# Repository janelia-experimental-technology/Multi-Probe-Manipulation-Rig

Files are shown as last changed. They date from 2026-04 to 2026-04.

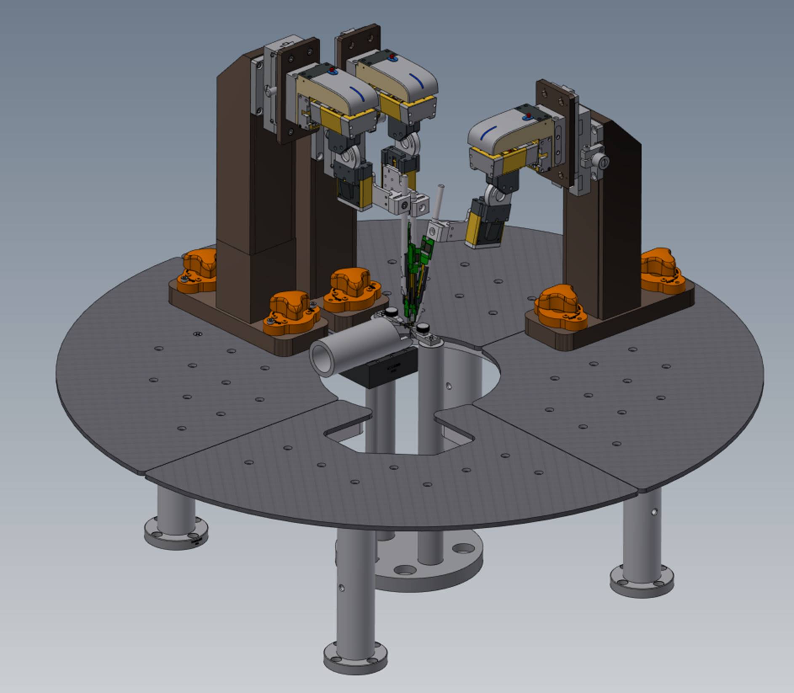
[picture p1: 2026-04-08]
Manipulator Rig.jpg

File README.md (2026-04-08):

### Multi-probe Manipulation Rig

Neural probe manipulation requires precise manipulation to avoid errors and optimize good placement for signal development. Janelia researchers and the Janelia Experimental Technology group have developed a multi-probe manipulation rig for such experiments with rodents. The base surface is magnetic stainless steel and the manipulator towers can be freely moved then locked in place with magnetic clamps for rough positioning. Sensapex 3 axis micromanipulators then provide precise positioning. Adapter designs for the manipulator include holders for Neuropixels probes.   

Opportunity: Free to make for Non-Profit Research by downloading the design here. See included hardware license.

Rights and designs available for Commercial License. Janelia makes no endorsements or guarantees of licensee products.

For inquiries, please contact innovation@janelia.hhmi.org and reference this repository.

To cite the designs, please use DOI: https://doi.org/10.25378/janelia.31964007

Supersedes Flintbox ID: 2020-004

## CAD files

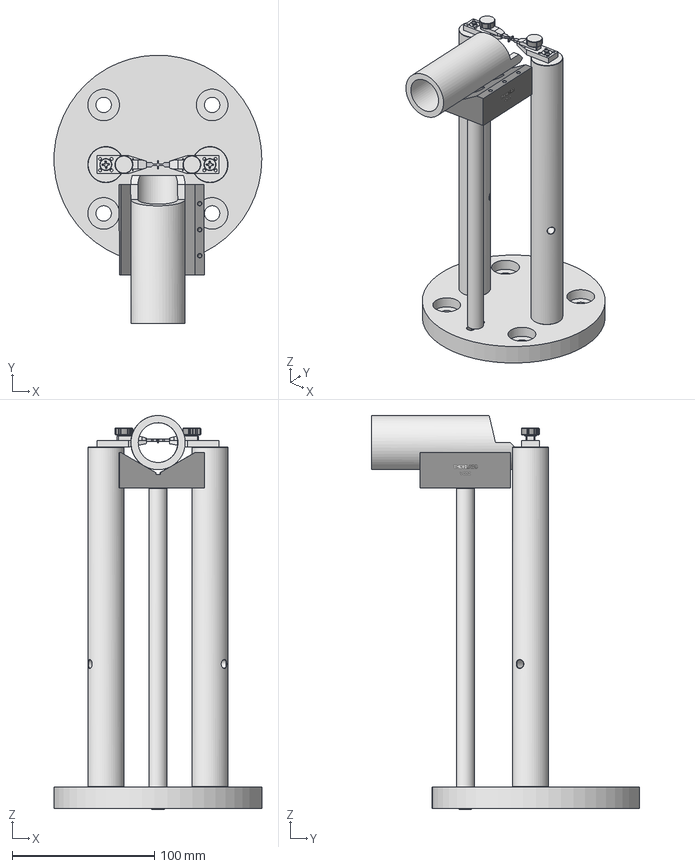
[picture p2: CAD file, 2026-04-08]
ASSEMBLY DRAWINGS AND MODEL/J008192 PTR V2 HEAD POST AND MOUNTING BARS Rev -.stp
145.9 x 188.6 x 276.8 mm
J005774 x 2
J005776 x 2
91771A197 x 2
92141A009 x 2
91185A440 x 2
91841A009 x 2
J007751 x 2
VC3C
PTR Mouse Tube
J008194
J007279
J006229
92240A539 x 2
92196A539

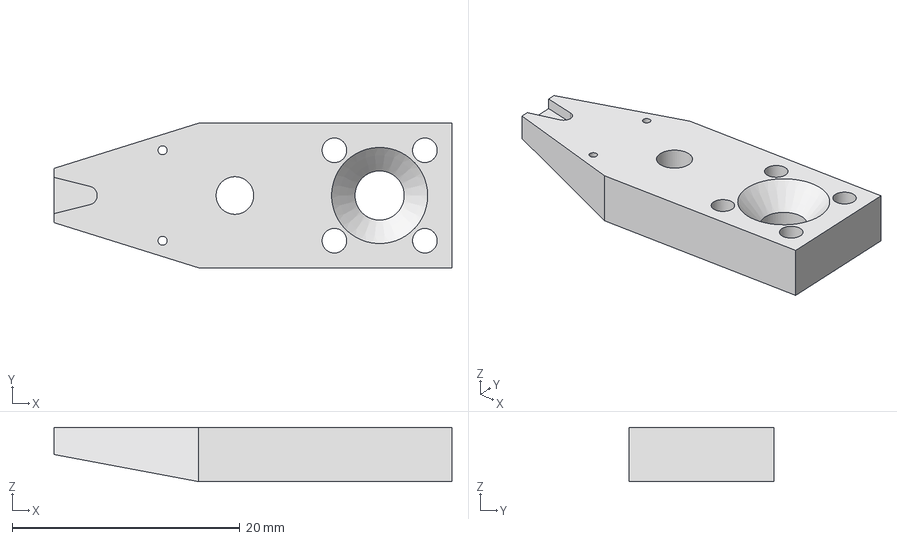
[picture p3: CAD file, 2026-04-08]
PART DRAWINGS AND MODELS/J005774 HeadPostHolderBottom Rev -.stp
34.9 x 12.7 x 4.76 mm

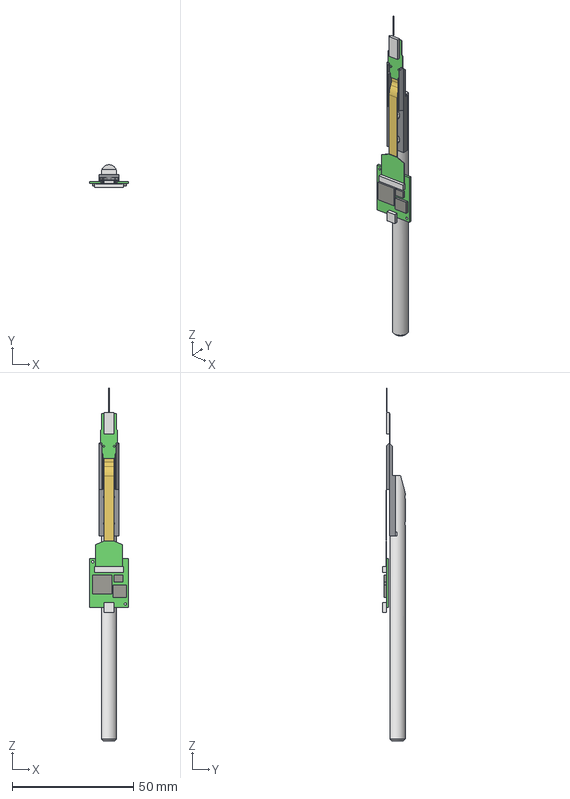
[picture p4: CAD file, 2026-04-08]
ASSEMBLY DRAWINGS AND MODEL/J007802 NEUROPIXELS 3A ENGINEERING PROTOTYPE PROBE AND ROD HOLDER Rev -.stp
16.0 x 9.32 x 145.3 mm
NEUROPIXEL HEADSTAGE PCB
J007803
J007626
92010A003 x 2

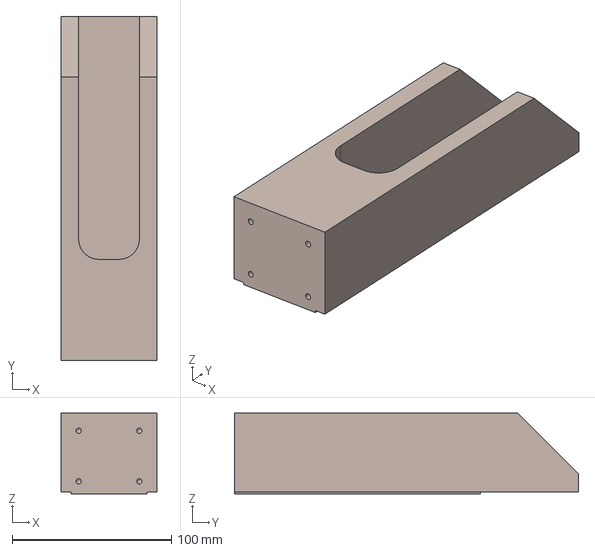
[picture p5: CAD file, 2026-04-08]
PART DRAWINGS AND MODELS/J007471 PTR V2 Z MOUNT Rev -.stp
60.3 x 215.9 x 50.8 mm

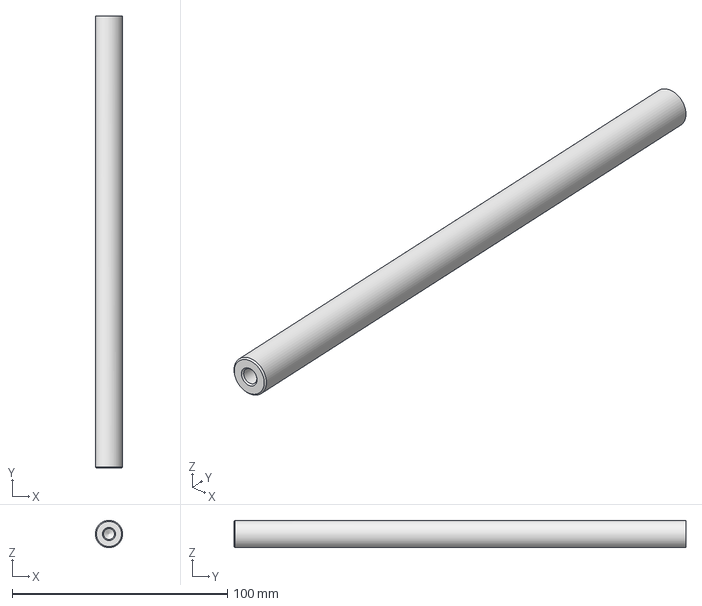
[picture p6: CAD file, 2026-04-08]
PART DRAWINGS AND MODELS/J008194 TR10-AI Rev -.stp
12.7 x 210.0 x 12.7 mm

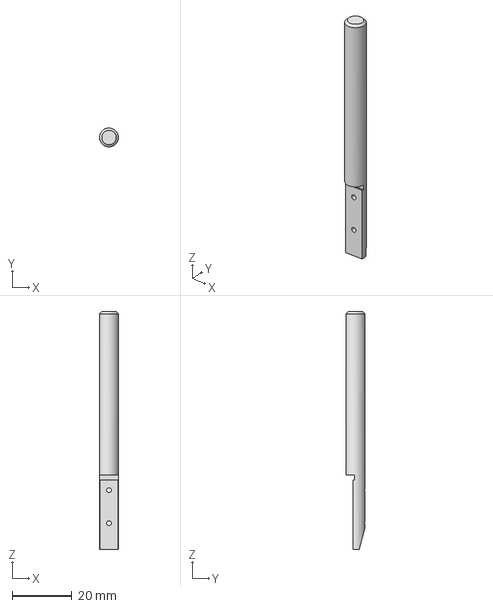
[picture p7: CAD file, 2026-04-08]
PART DRAWINGS AND MODELS/J007474 PTR PROBE MOUNT ROD Rev -.stp
6.35 x 6.35 x 79.4 mm

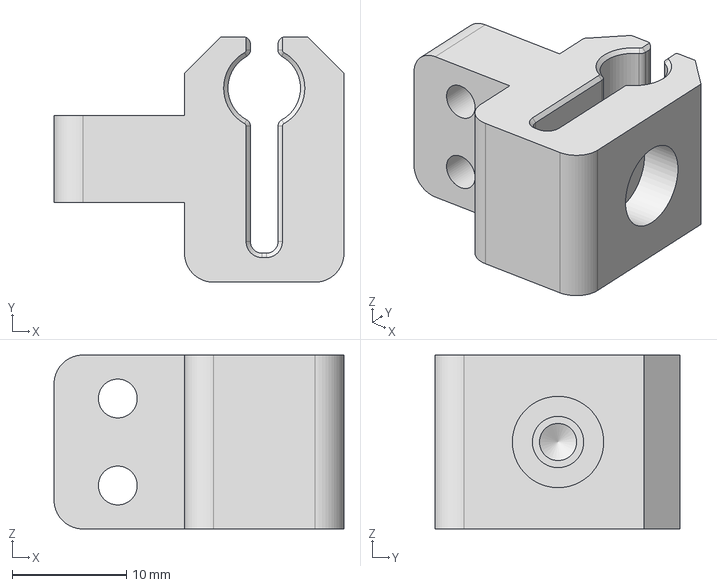
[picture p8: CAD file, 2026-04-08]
PART DRAWINGS AND MODELS/J007475 PTR V2 ROD MOUNT 0_250 DIA Rev -.stp
25.4 x 21.5 x 15.2 mm

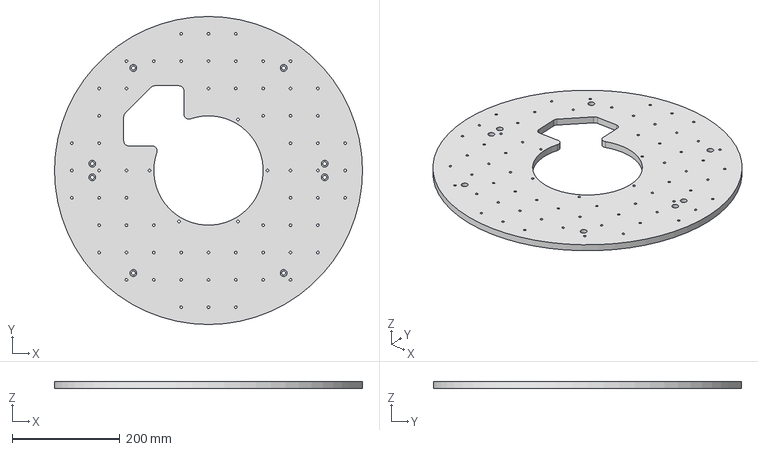
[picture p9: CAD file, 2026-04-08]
PART DRAWINGS AND MODELS/J006218 PTR RAISED PLATFORM Rev A.stp
572.3 x 572.3 x 12.7 mm

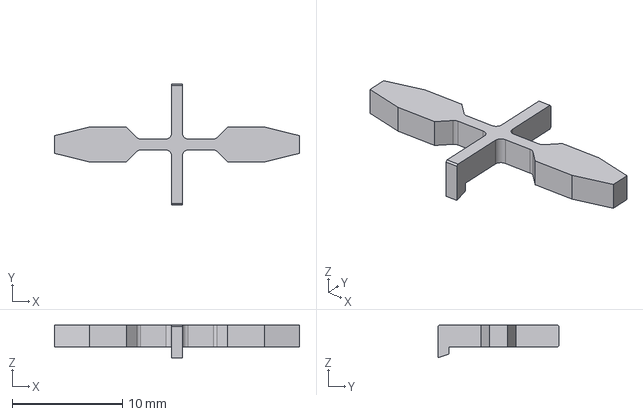
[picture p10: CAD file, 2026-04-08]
PART DRAWINGS AND MODELS/J007279 NARROWED CENTER X HEADBAR Rev -.stp
22.2 x 11.0 x 2.96 mm

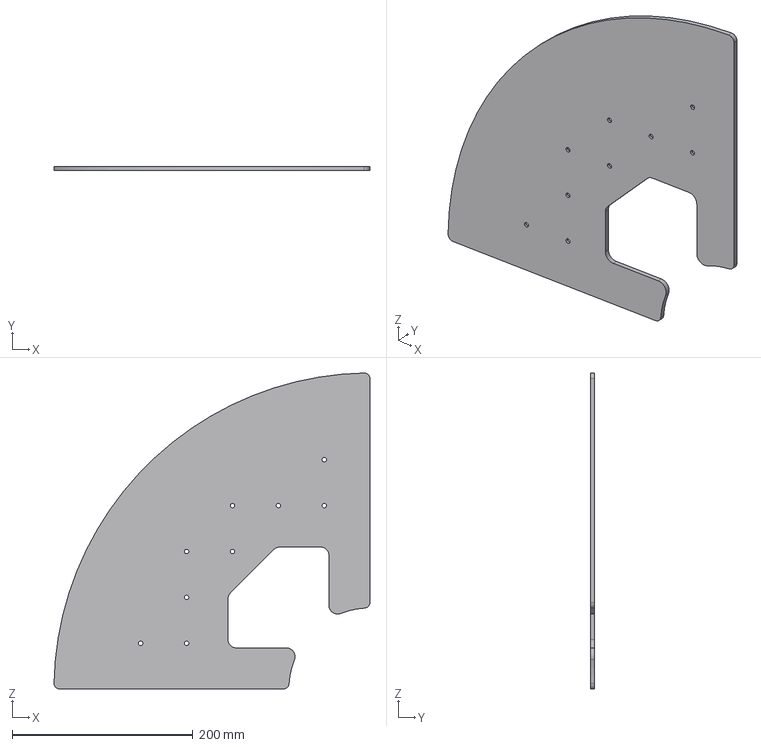
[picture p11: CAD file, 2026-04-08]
PART DRAWINGS AND MODELS/J007541 PTR MBASE CUTOUT Rev -.stp
349.7 x 4.76 x 349.7 mm

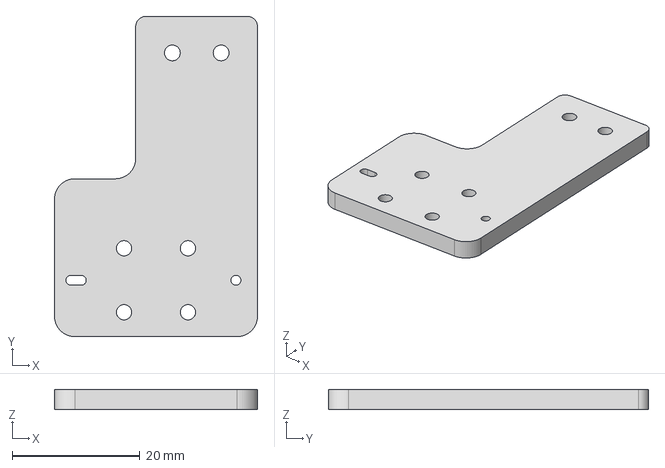
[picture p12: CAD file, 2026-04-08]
PART DRAWINGS AND MODELS/J007476 PTR MANIPULATOR OFFSET PLATE Rev -.stp
31.8 x 50.1 x 3.17 mm

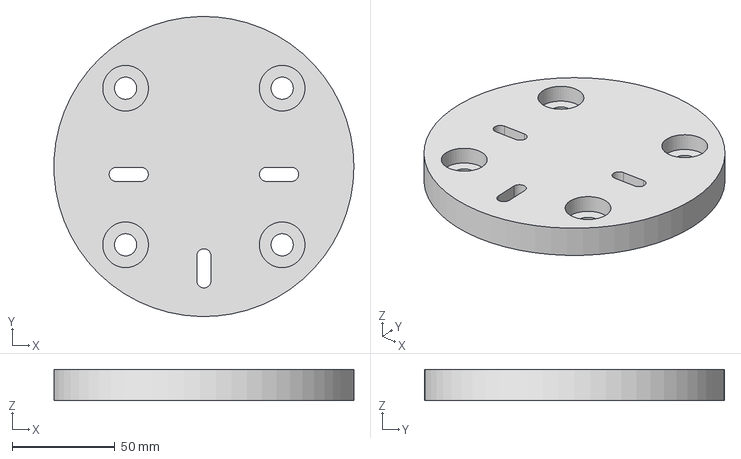
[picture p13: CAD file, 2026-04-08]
PART DRAWINGS AND MODELS/J006229 PTR CENTER Rev -.stp
145.9 x 146.0 x 15.2 mm

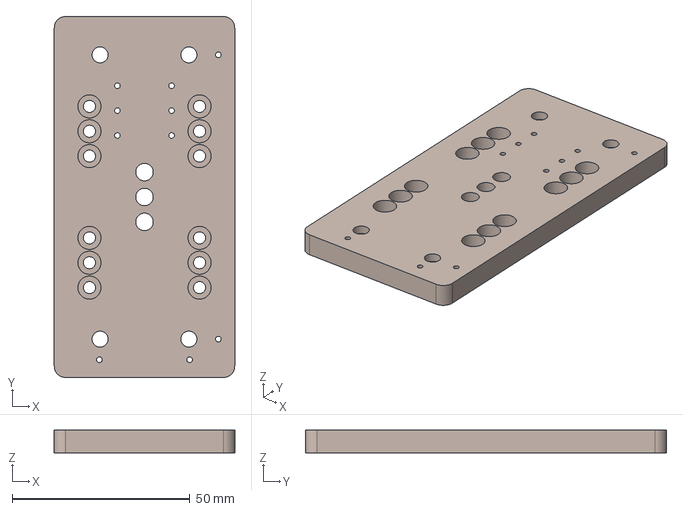
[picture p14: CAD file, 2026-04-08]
PART DRAWINGS AND MODELS/J007472 PTR V2 MAN Z BASE PLATE Rev A.stp
50.8 x 101.6 x 6.35 mm

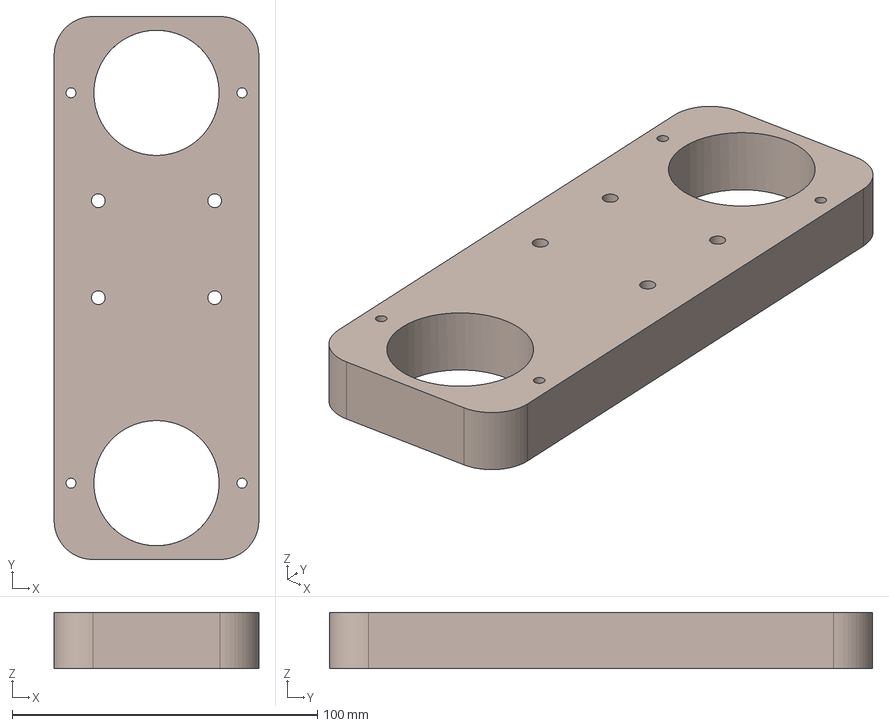
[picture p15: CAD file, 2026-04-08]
PART DRAWINGS AND MODELS/J007473 PTR V2 LOWER MBASE Rev A.stp
67.1 x 177.8 x 18.4 mm

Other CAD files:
PART DRAWINGS AND MODELS/J007478 PTR MBASE Rev -.stp
PART DRAWINGS AND MODELS/J005776 HeadPostHolderTop Rev -.stp
PART DRAWINGS AND MODELS/J007803 NEUROPIXEL 3A PROBE BASE Rev -.stp
PART DRAWINGS AND MODELS/J007631 PTR V2 Z SPACER Rev -.stp
PART DRAWINGS AND MODELS/J007626 PTR PROBE MOUNT ROD EXTENDED Rev -.stp
PART DRAWINGS AND MODELS/J007751 RS12-AI Rev -.stp
PART DRAWINGS AND MODELS/J007803 NEUROPIXEL 3A PROBE BASE Rev -.stl

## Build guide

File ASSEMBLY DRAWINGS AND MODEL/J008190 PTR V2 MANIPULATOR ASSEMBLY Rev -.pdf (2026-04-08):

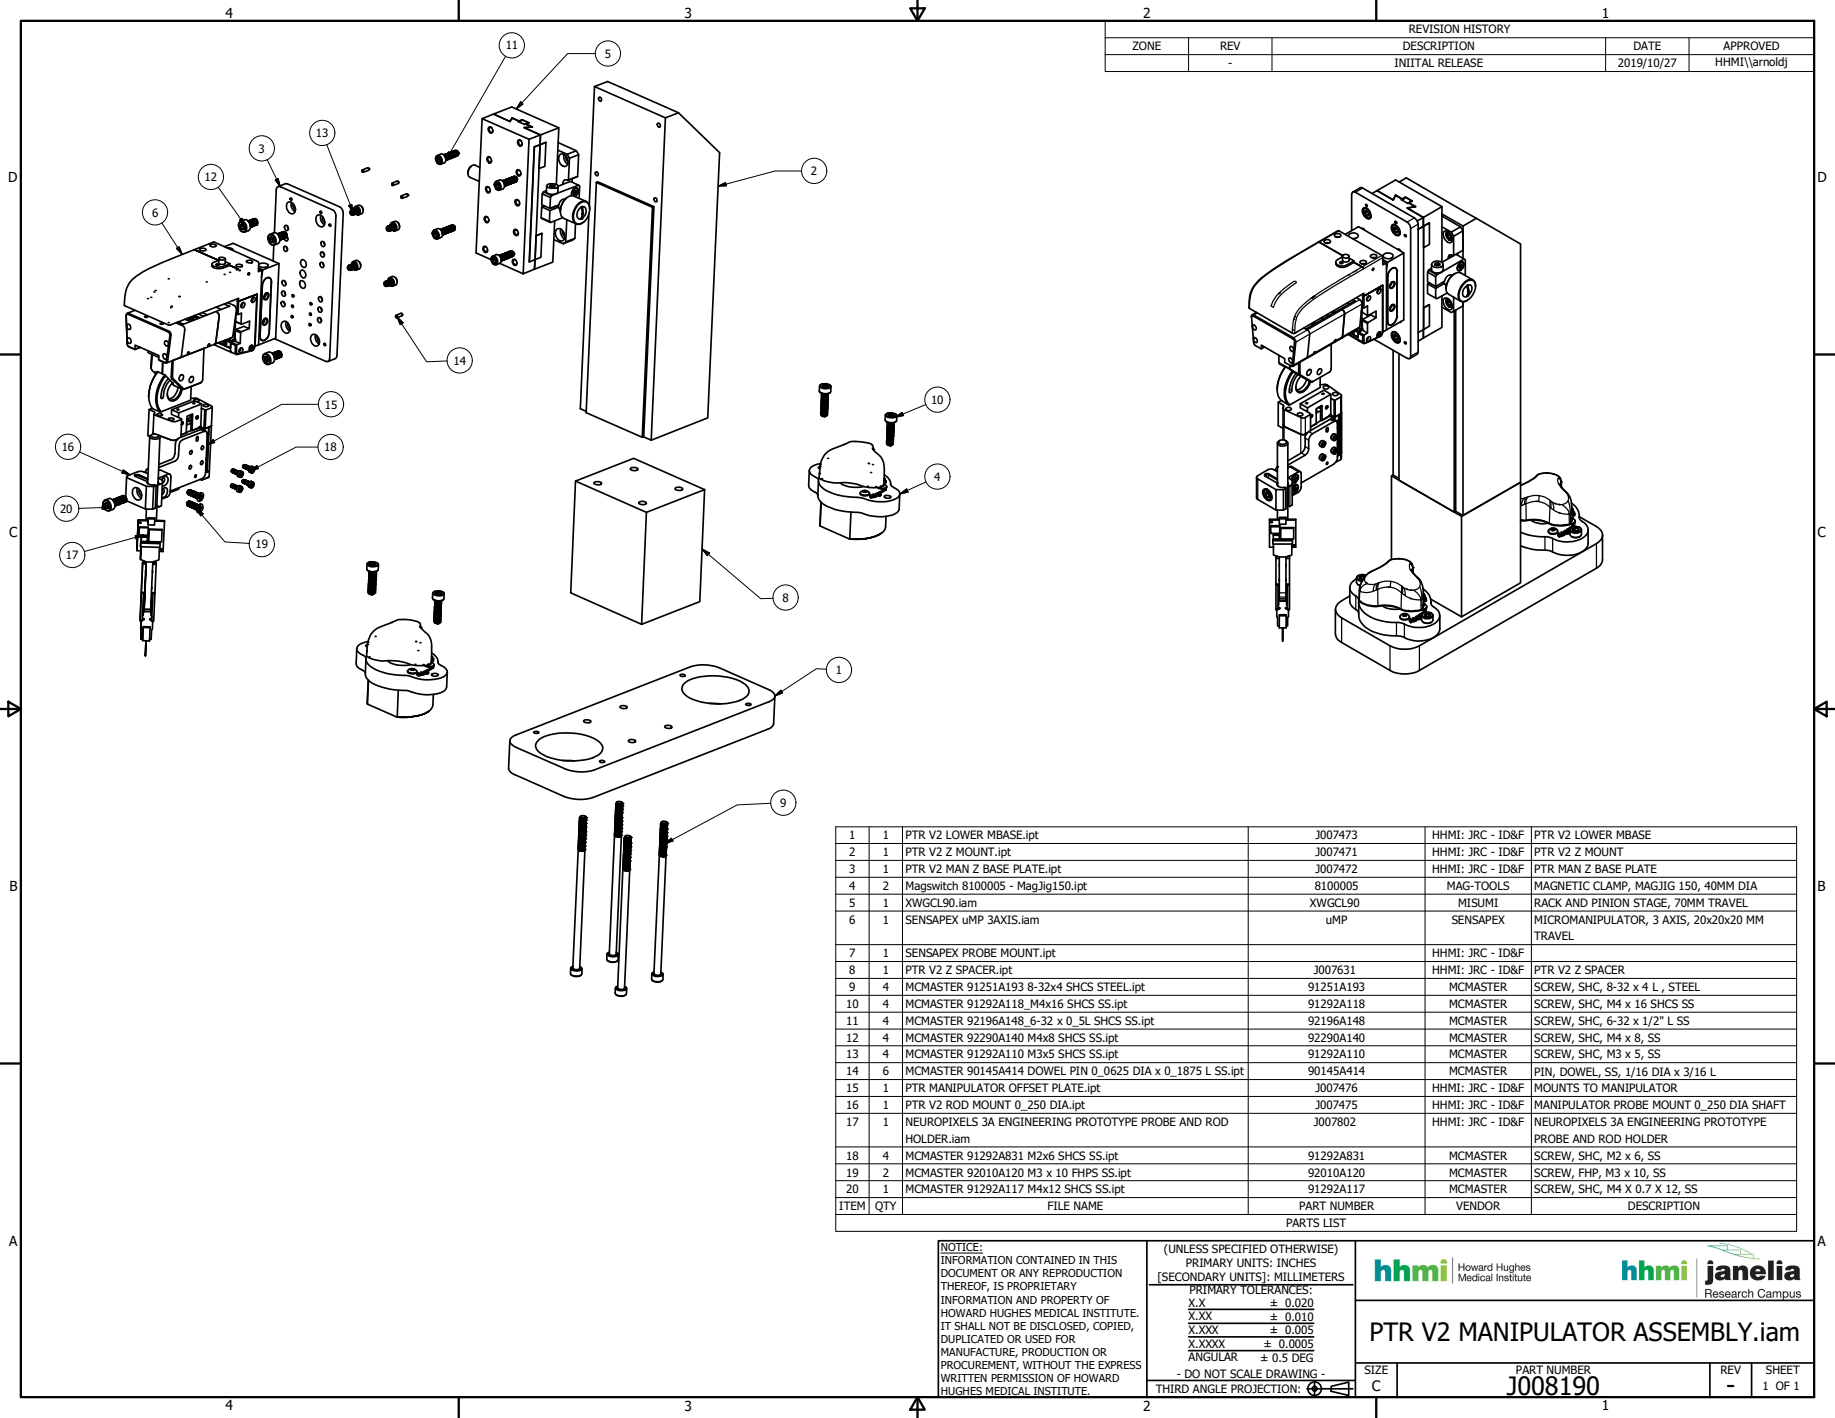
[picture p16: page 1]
PARTS LIST; PART NUMBER; 1 OF 1 THIRD ANGLE PROJECTION:; ± 0.020 ± 0.010 ± 0.005 ± 0.0005 ± 0.5 DEG; REVISION HISTORY

ZONE | REV | DESCRIPTION | DATE | APPROVED

- | INIITAL RELEASE | 2019/10/27 | HHMI\\arnoldj

1 | 1 | PTR V2 LOWER MBASE.ipt | J007473 | HHMI: JRC - ID&F | PTR V2 LOWER MBASE
2 | 1 | PTR V2 Z MOUNT.ipt | J007471 | HHMI: JRC - ID&F | PTR V2 Z MOUNT
3 | 1 | PTR V2 MAN Z BASE PLATE.ipt | J007472 | HHMI: JRC - ID&F | PTR MAN Z BASE PLATE
4 | 2 | Magswitch 8100005 - MagJig150.ipt | 8100005 | MAG-TOOLS | MAGNETIC CLAMP, MAGJIG 150, 40MM DIA
5 | 1 | XWGCL90.iam | XWGCL90 | MISUMI | RACK AND PINION STAGE, 70MM TRAVEL
6 | 1 | SENSAPEX uMP 3AXIS.iam | uMP | SENSAPEX | MICROMANIPULATOR, 3 AXIS, 20x20x20 MM TRAVEL

7 | 1 | SENSAPEX PROBE MOUNT.ipt | | HHMI: JRC - ID&F
8 | 1 | PTR V2 Z SPACER.ipt | J007631 | HHMI: JRC - ID&F | PTR V2 Z SPACER
9 | 4 | MCMASTER 91251A193 8-32x4 SHCS STEEL.ipt | 91251A193 | MCMASTER | SCREW, SHC, 8-32 x 4 L , STEEL
10 | 4 | MCMASTER 91292A118_M4x16 SHCS SS.ipt | 91292A118 | MCMASTER | SCREW, SHC, M4 x 16 SHCS SS
11 | 4 | MCMASTER 92196A148_6-32 x 0_5L SHCS SS.ipt | 92196A148 | MCMASTER | SCREW, SHC, 6-32 x 1/2" L SS
12 | 4 | MCMASTER 92290A140 M4x8 SHCS SS.ipt | 92290A140 | MCMASTER | SCREW, SHC, M4 x 8, SS
13 | 4 | MCMASTER 91292A110 M3x5 SHCS SS.ipt | 91292A110 | MCMASTER | SCREW, SHC, M3 x 5, SS
14 | 6 | MCMASTER 90145A414 DOWEL PIN 0_0625 DIA x 0_1875 L SS.ipt | 90145A414 | MCMASTER | PIN, DOWEL, SS, 1/16 DIA x 3/16 L
15 | 1 | PTR MANIPULATOR OFFSET PLATE.ipt | J007476 | HHMI: JRC - ID&F | MOUNTS TO MANIPULATOR
16 | 1 | PTR V2 ROD MOUNT 0_250 DIA.ipt | J007475 | HHMI: JRC - ID&F | MANIPULATOR PROBE MOUNT 0_250 DIA SHAFT
17 | 1 | NEUROPIXELS 3A ENGINEERING PROTOTYPE PROBE AND ROD HOLDER.iam | J007802 | HHMI: JRC - ID&F | NEUROPIXELS 3A ENGINEERING PROTOTYPE PROBE AND ROD HOLDER

18 | 4 | MCMASTER 91292A831 M2x6 SHCS SS.ipt | 91292A831 | MCMASTER | SCREW, SHC, M2 x 6, SS
19 | 2 | MCMASTER 92010A120 M3 x 10 FHPS SS.ipt | 92010A120 | MCMASTER | SCREW, FHP, M3 x 10, SS
20 | 1 | MCMASTER 91292A117 M4x12 SHCS SS.ipt | 91292A117 | MCMASTER | SCREW, SHC, M4 X 0.7 X 12, SS
ITEM | QTY | FILE NAME | PART NUMBER | VENDOR | DESCRIPTION

NOTICE:
INFORMATION CONTAINED IN THIS
DOCUMENT OR ANY REPRODUCTION
THEREOF, IS PROPRIETARY
INFORMATION AND PROPERTY OF
HOWARD HUGHES MEDICAL INSTITUTE.
IT SHALL NOT BE DISCLOSED, COPIED,
DUPLICATED OR USED FOR
MANUFACTURE, PRODUCTION OR
PROCUREMENT, WITHOUT THE EXPRESS
WRITTEN PERMISSION OF HOWARD
HUGHES MEDICAL INSTITUTE.

(UNLESS SPECIFIED OTHERWISE)
PRIMARY UNITS: INCHES
[SECONDARY UNITS]: MILLIMETERS
PRIMARY TOLERANCES:
X.XXX
X.XXXX
ANGULAR
- DO NOT SCALE DRAWING -

PTR V2 MANIPULATOR ASSEMBLY.iam

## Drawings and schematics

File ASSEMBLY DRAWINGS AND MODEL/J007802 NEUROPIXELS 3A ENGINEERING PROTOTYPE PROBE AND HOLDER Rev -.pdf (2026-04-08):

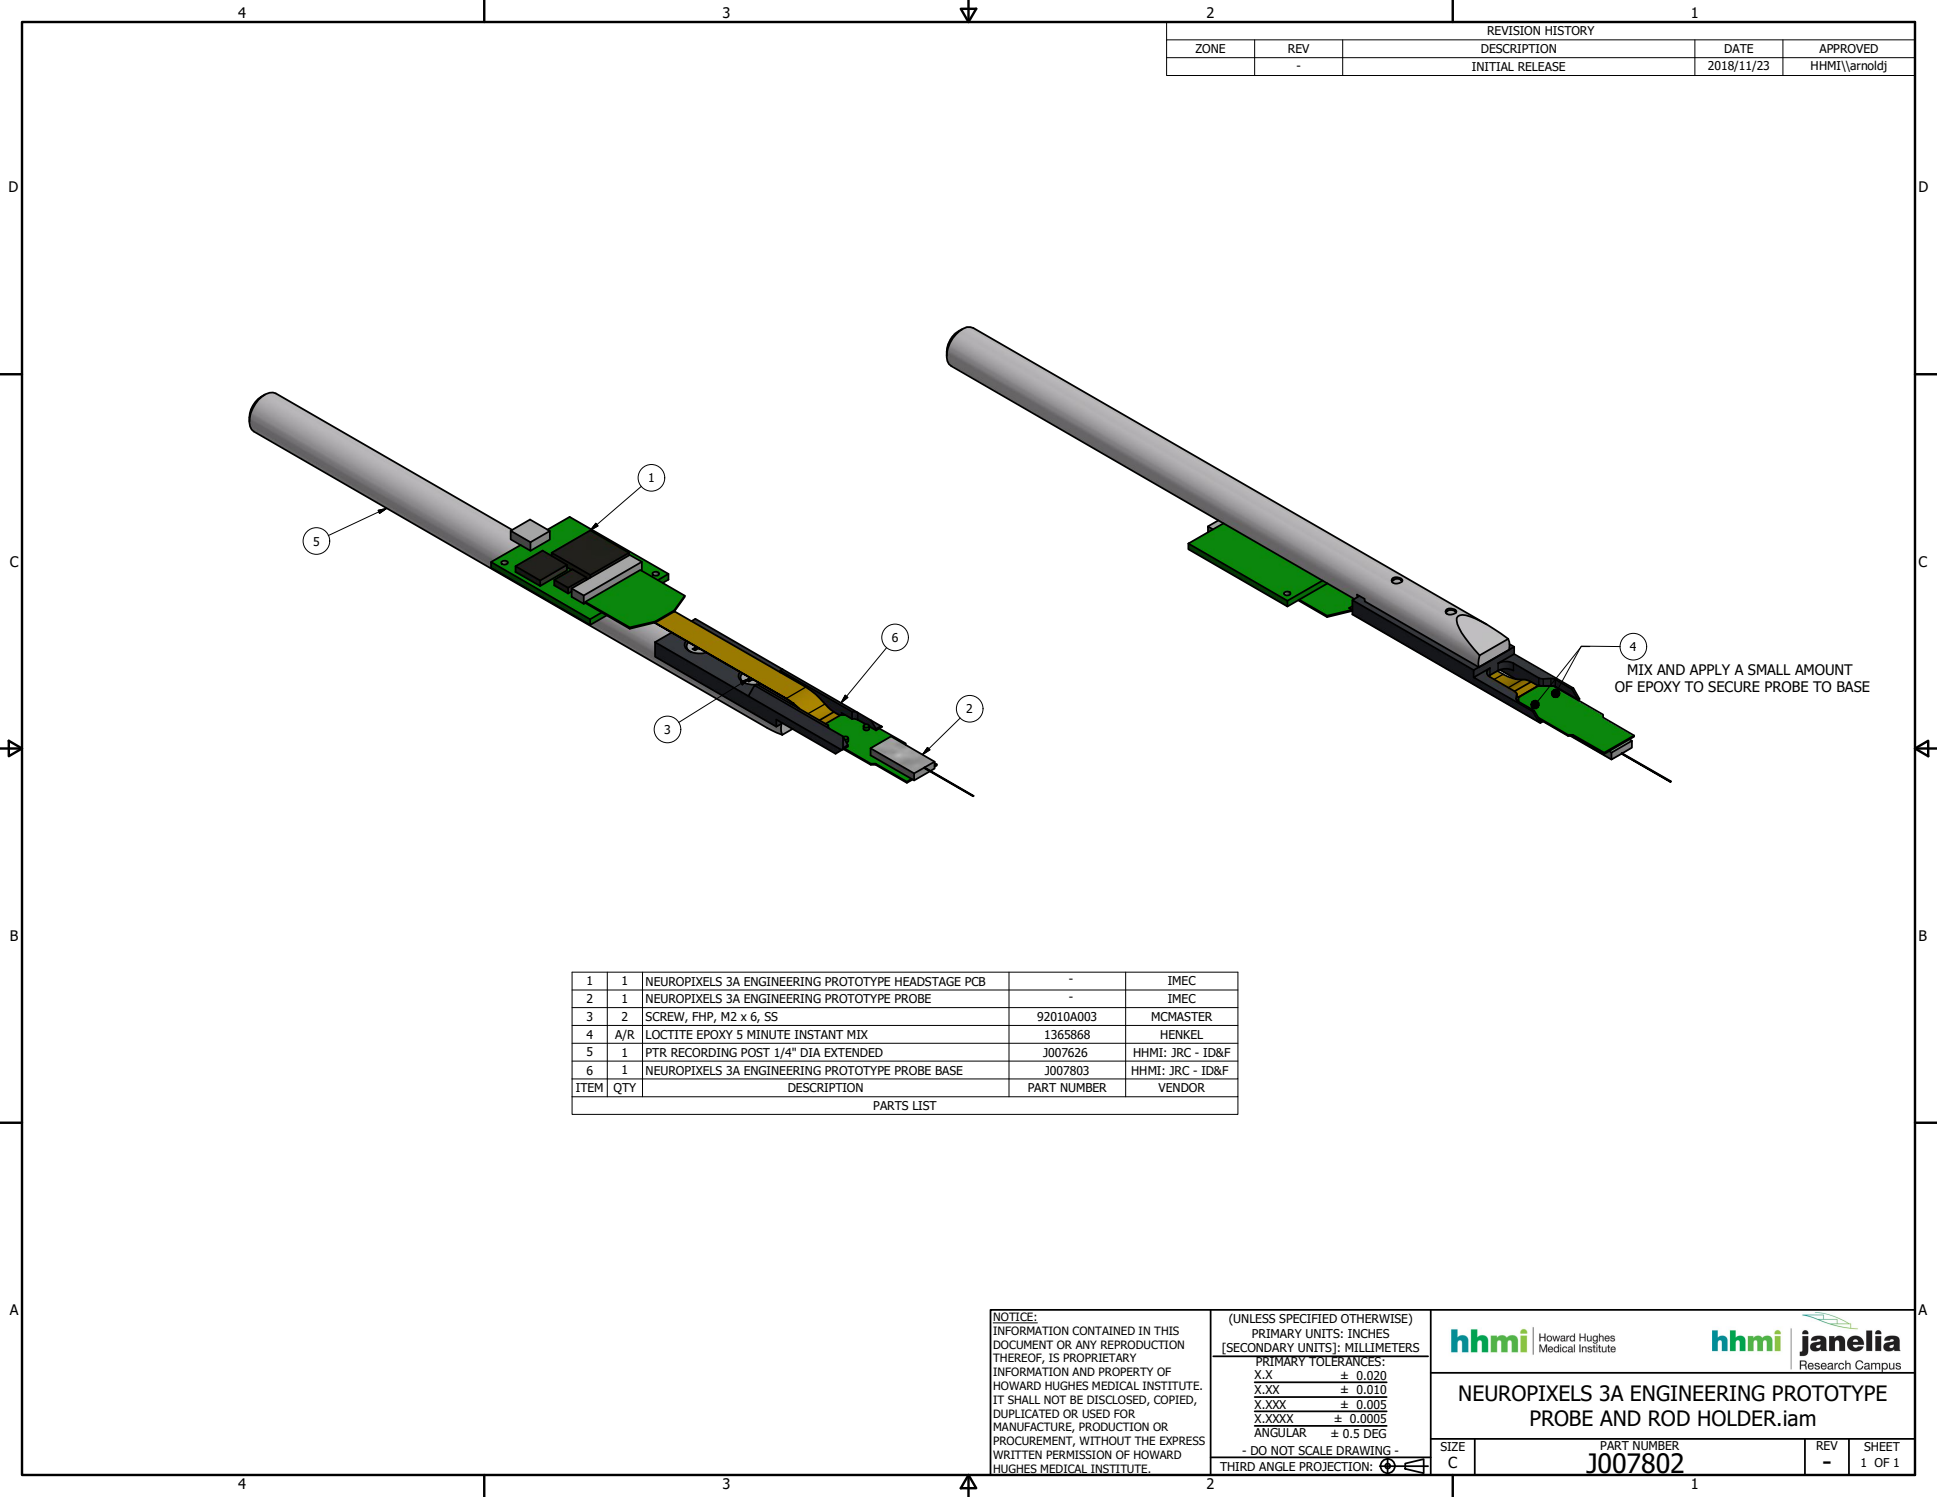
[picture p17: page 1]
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

ZONE | REV | DESCRIPTION | DATE | APPROVED

- | INITIAL RELEASE | 2018/11/23 | HHMI\\arnoldj

MIX AND APPLY A SMALL AMOUNT
OF EPOXY TO SECURE PROBE TO BASE

1 | 1 | NEUROPIXELS 3A ENGINEERING PROTOTYPE HEADSTAGE PCB | - | IMEC
2 | 1 | NEUROPIXELS 3A ENGINEERING PROTOTYPE PROBE | - | IMEC
3 | 2 | SCREW, FHP, M2 x 6, SS | 92010A003 | MCMASTER
4 | A/R | LOCTITE EPOXY 5 MINUTE INSTANT MIX | 1365868 | HENKEL
5 | 1 | PTR RECORDING POST 1/4" DIA EXTENDED | J007626 | HHMI: JRC - ID&F
6 | 1 | NEUROPIXELS 3A ENGINEERING PROTOTYPE PROBE BASE | J007803 | HHMI: JRC - ID&F
ITEM | QTY | DESCRIPTION | PART NUMBER | VENDOR

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

NEUROPIXELS 3A ENGINEERING PROTOTYPE

PROBE AND ROD HOLDER.iam

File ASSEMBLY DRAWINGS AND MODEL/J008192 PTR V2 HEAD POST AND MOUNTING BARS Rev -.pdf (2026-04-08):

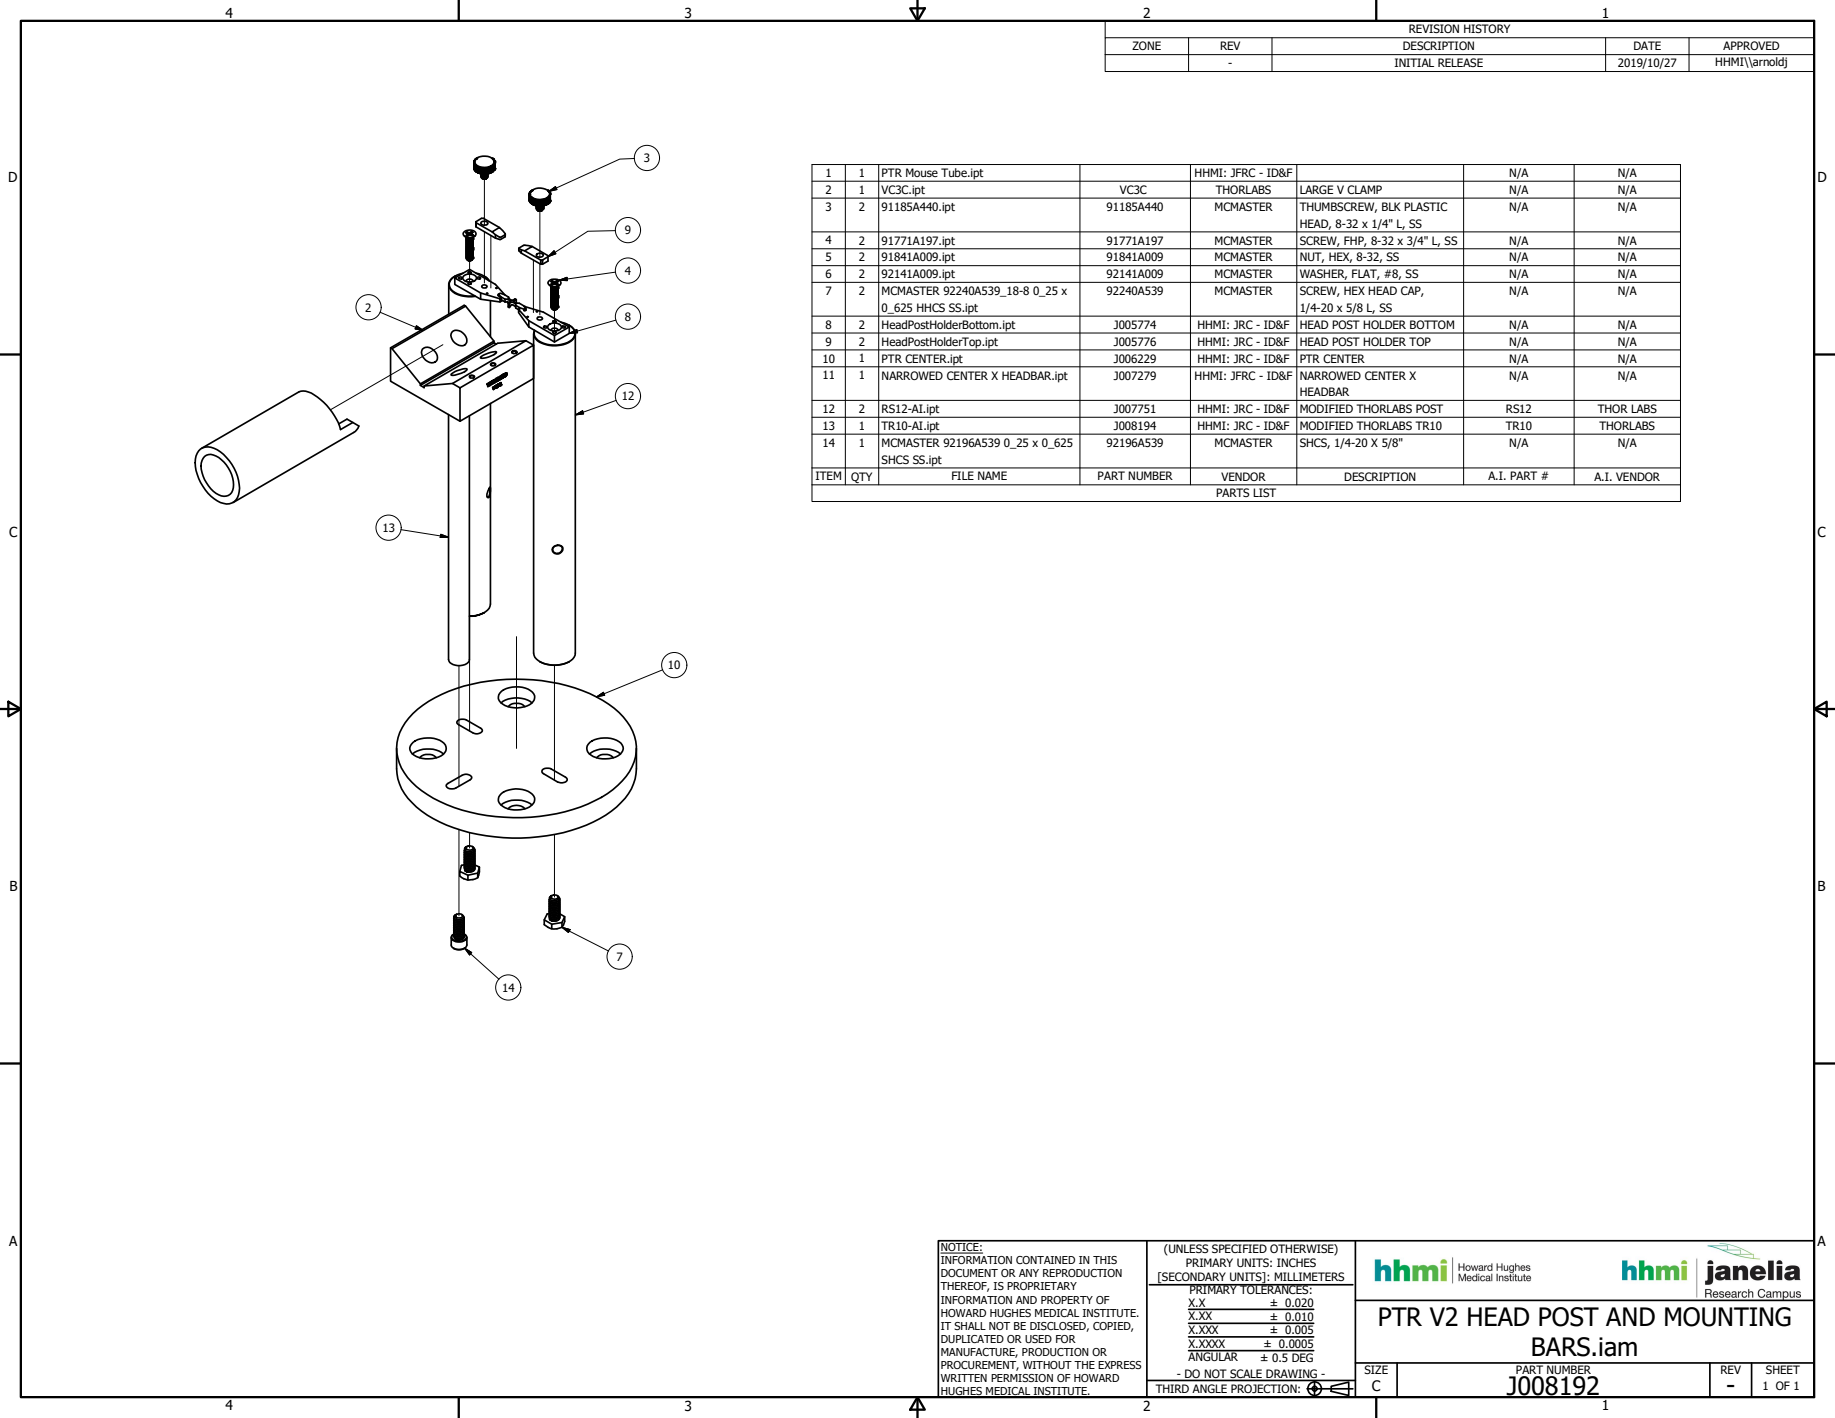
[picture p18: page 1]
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

ZONE | REV | DESCRIPTION | DATE | APPROVED

- | INITIAL RELEASE | 2019/10/27 | HHMI\\arnoldj

1 | 1 | PTR Mouse Tube.ipt | | HHMI: JFRC - ID&F | | N/A | N/A
2 | 1 | VC3C.ipt | VC3C | THORLABS | LARGE V CLAMP | N/A | N/A
3 | 2 | 91185A440.ipt | 91185A440 | MCMASTER | THUMBSCREW, BLK PLASTIC HEAD, 8-32 x 1/4" L, SS | N/A | N/A

4 | 2 | 91771A197.ipt | 91771A197 | MCMASTER | SCREW, FHP, 8-32 x 3/4" L, SS | N/A | N/A
5 | 2 | 91841A009.ipt | 91841A009 | MCMASTER | NUT, HEX, 8-32, SS | N/A | N/A
6 | 2 | 92141A009.ipt | 92141A009 | MCMASTER | WASHER, FLAT, #8, SS | N/A | N/A
7 | 2 | MCMASTER 92240A539_18-8 0_25 x 0_625 HHCS SS.ipt | 92240A539 | MCMASTER | SCREW, HEX HEAD CAP, 1/4-20 x 5/8 L, SS | N/A | N/A

8 | 2 | HeadPostHolderBottom.ipt | J005774 | HHMI: JRC - ID&F | HEAD POST HOLDER BOTTOM | N/A | N/A
9 | 2 | HeadPostHolderTop.ipt | J005776 | HHMI: JRC - ID&F | HEAD POST HOLDER TOP | N/A | N/A
10 | 1 | PTR CENTER.ipt | J006229 | HHMI: JRC - ID&F | PTR CENTER | N/A | N/A
11 | 1 | NARROWED CENTER X HEADBAR.ipt | J007279 | HHMI: JFRC - ID&F | NARROWED CENTER X HEADBAR | N/A | N/A

12 | 2 | RS12-AI.ipt | J007751 | HHMI: JRC - ID&F | MODIFIED THORLABS POST | RS12 | THOR LABS
13 | 1 | TR10-AI.ipt | J008194 | HHMI: JRC - ID&F | MODIFIED THORLABS TR10 | TR10 | THORLABS
14 | 1 | MCMASTER 92196A539 0_25 x 0_625 SHCS SS.ipt | 92196A539 | MCMASTER | SHCS, 1/4-20 X 5/8" | N/A | N/A

ITEM | QTY | FILE NAME | PART NUMBER | VENDOR | DESCRIPTION | A.I. PART # | A.I. VENDOR

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

PTR V2 HEAD POST AND MOUNTING

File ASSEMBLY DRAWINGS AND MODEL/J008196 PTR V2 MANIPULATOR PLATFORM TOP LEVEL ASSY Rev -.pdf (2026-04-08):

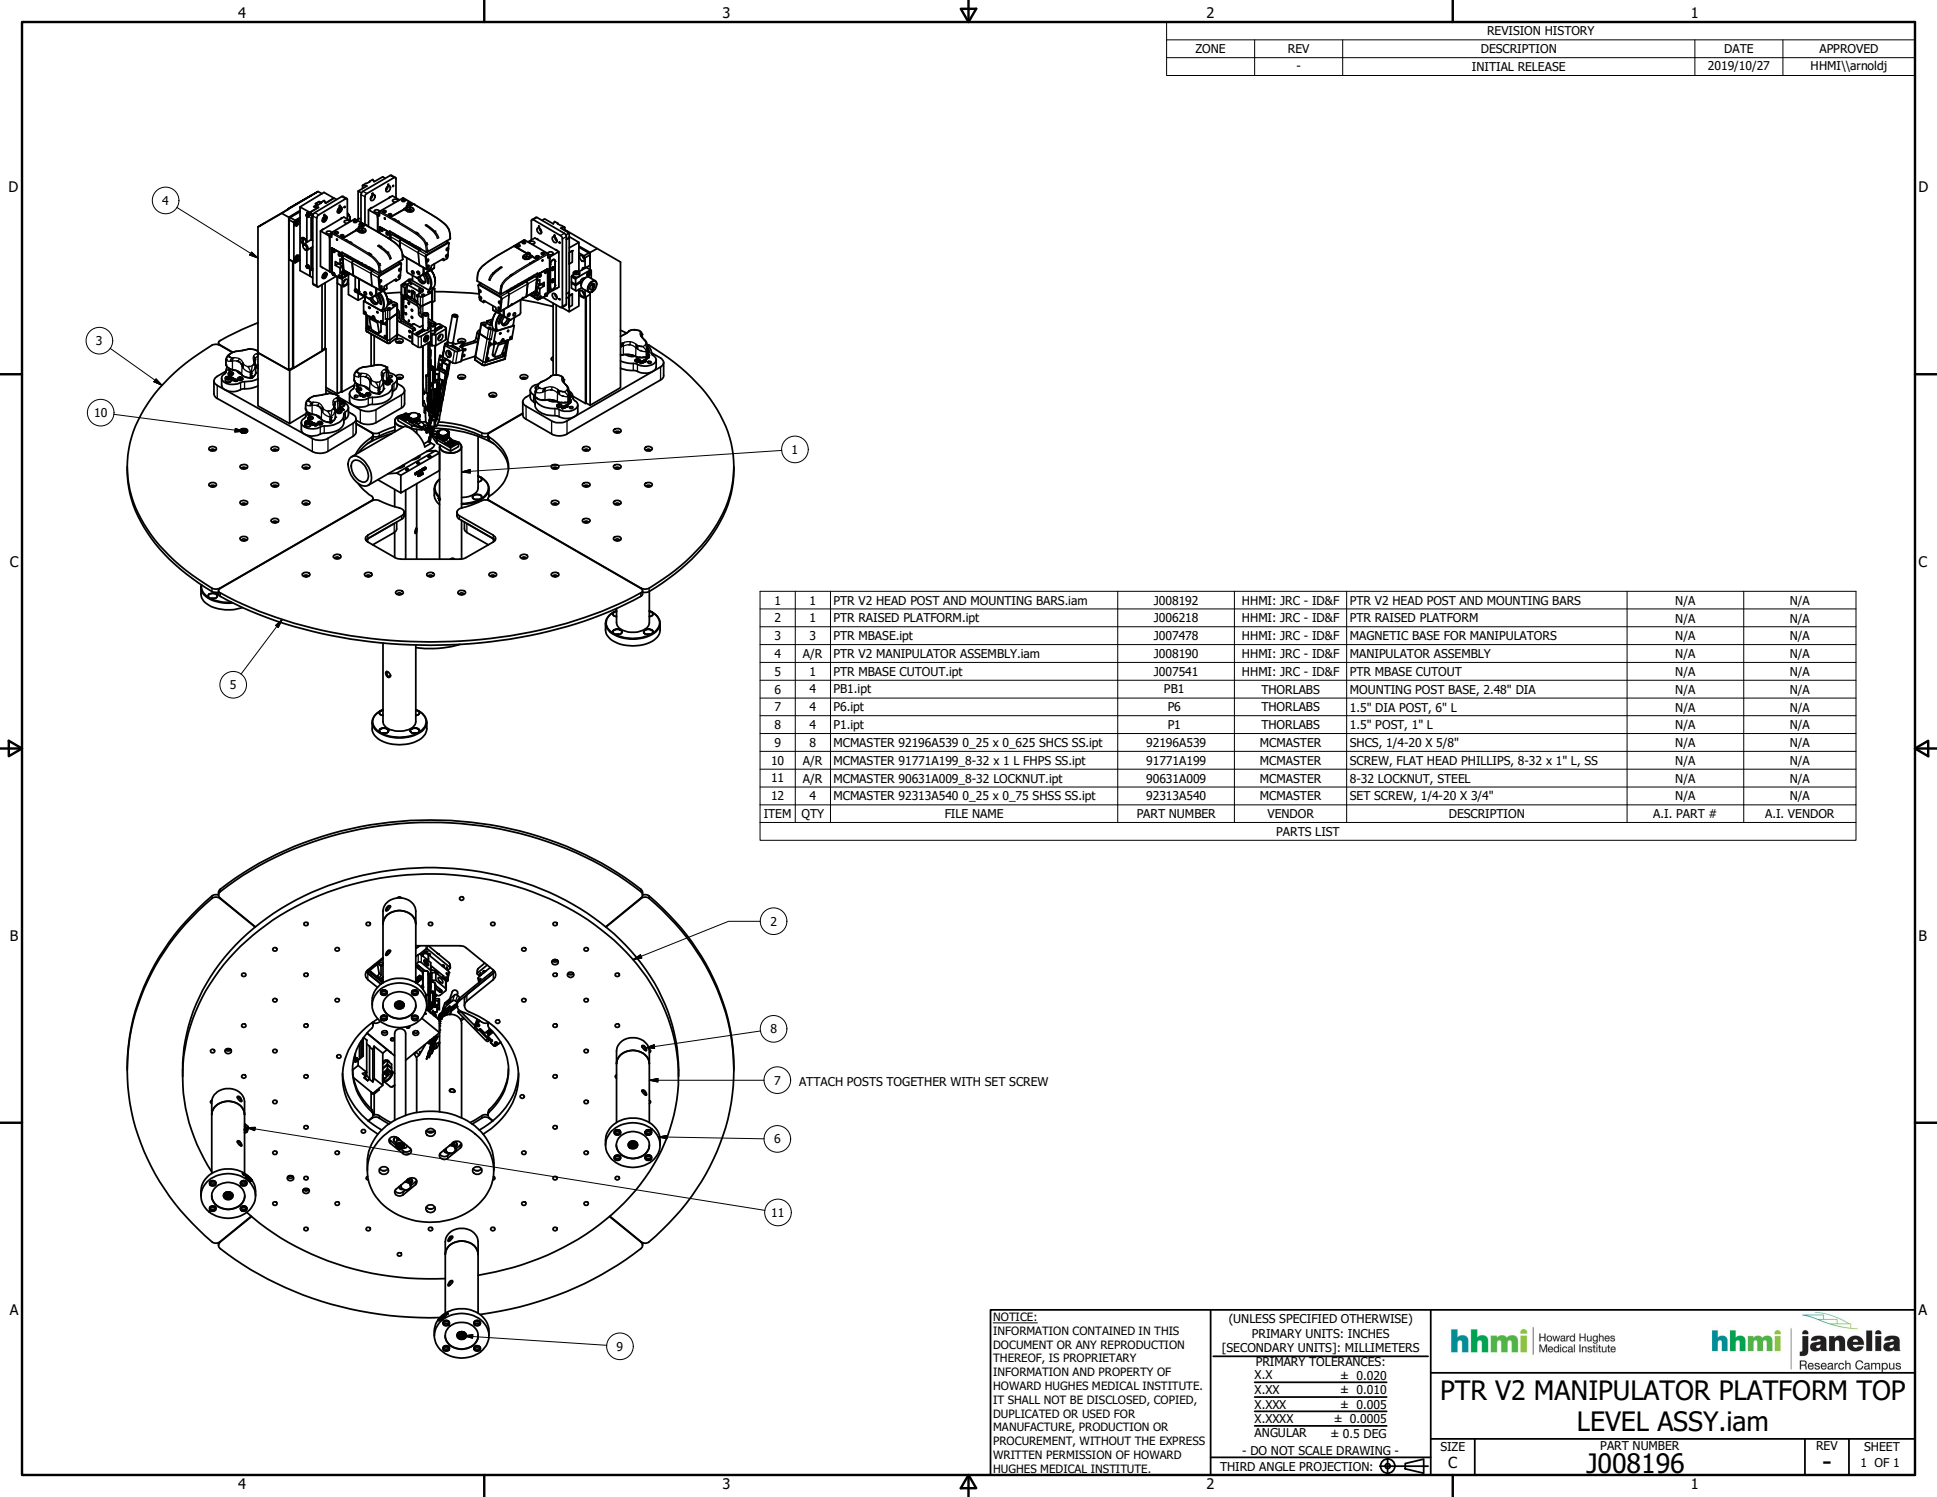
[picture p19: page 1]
PTR V2 HEAD POST AND MOUNTING BARS.iam; HHMI: JRC - ID&F PTR V2 HEAD POST AND MOUNTING BARS; PTR RAISED PLATFORM.ipt; HHMI: JRC - ID&F PTR RAISED PLATFORM; PTR MBASE.ipt; HHMI: JRC - ID&F MAGNETIC BASE FOR MANIPULATORS; A/R PTR V2 MANIPULATOR ASSEMBLY.iam; HHMI: JRC - ID&F MANIPULATOR ASSEMBLY; PTR MBASE CUTOUT.ipt; HHMI: JRC - ID&F PTR MBASE CUTOUT; PB1.ipt; THORLABS; MOUNTING POST BASE, 2.48" DIA; P6.ipt; 1.5" DIA POST, 6" L; P1.ipt; 1.5" POST, 1" L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

ATTACH POSTS TOGETHER WITH SET SCREW

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

PTR V2 MANIPULATOR PLATFORM TOP

LEVEL ASSY.iam

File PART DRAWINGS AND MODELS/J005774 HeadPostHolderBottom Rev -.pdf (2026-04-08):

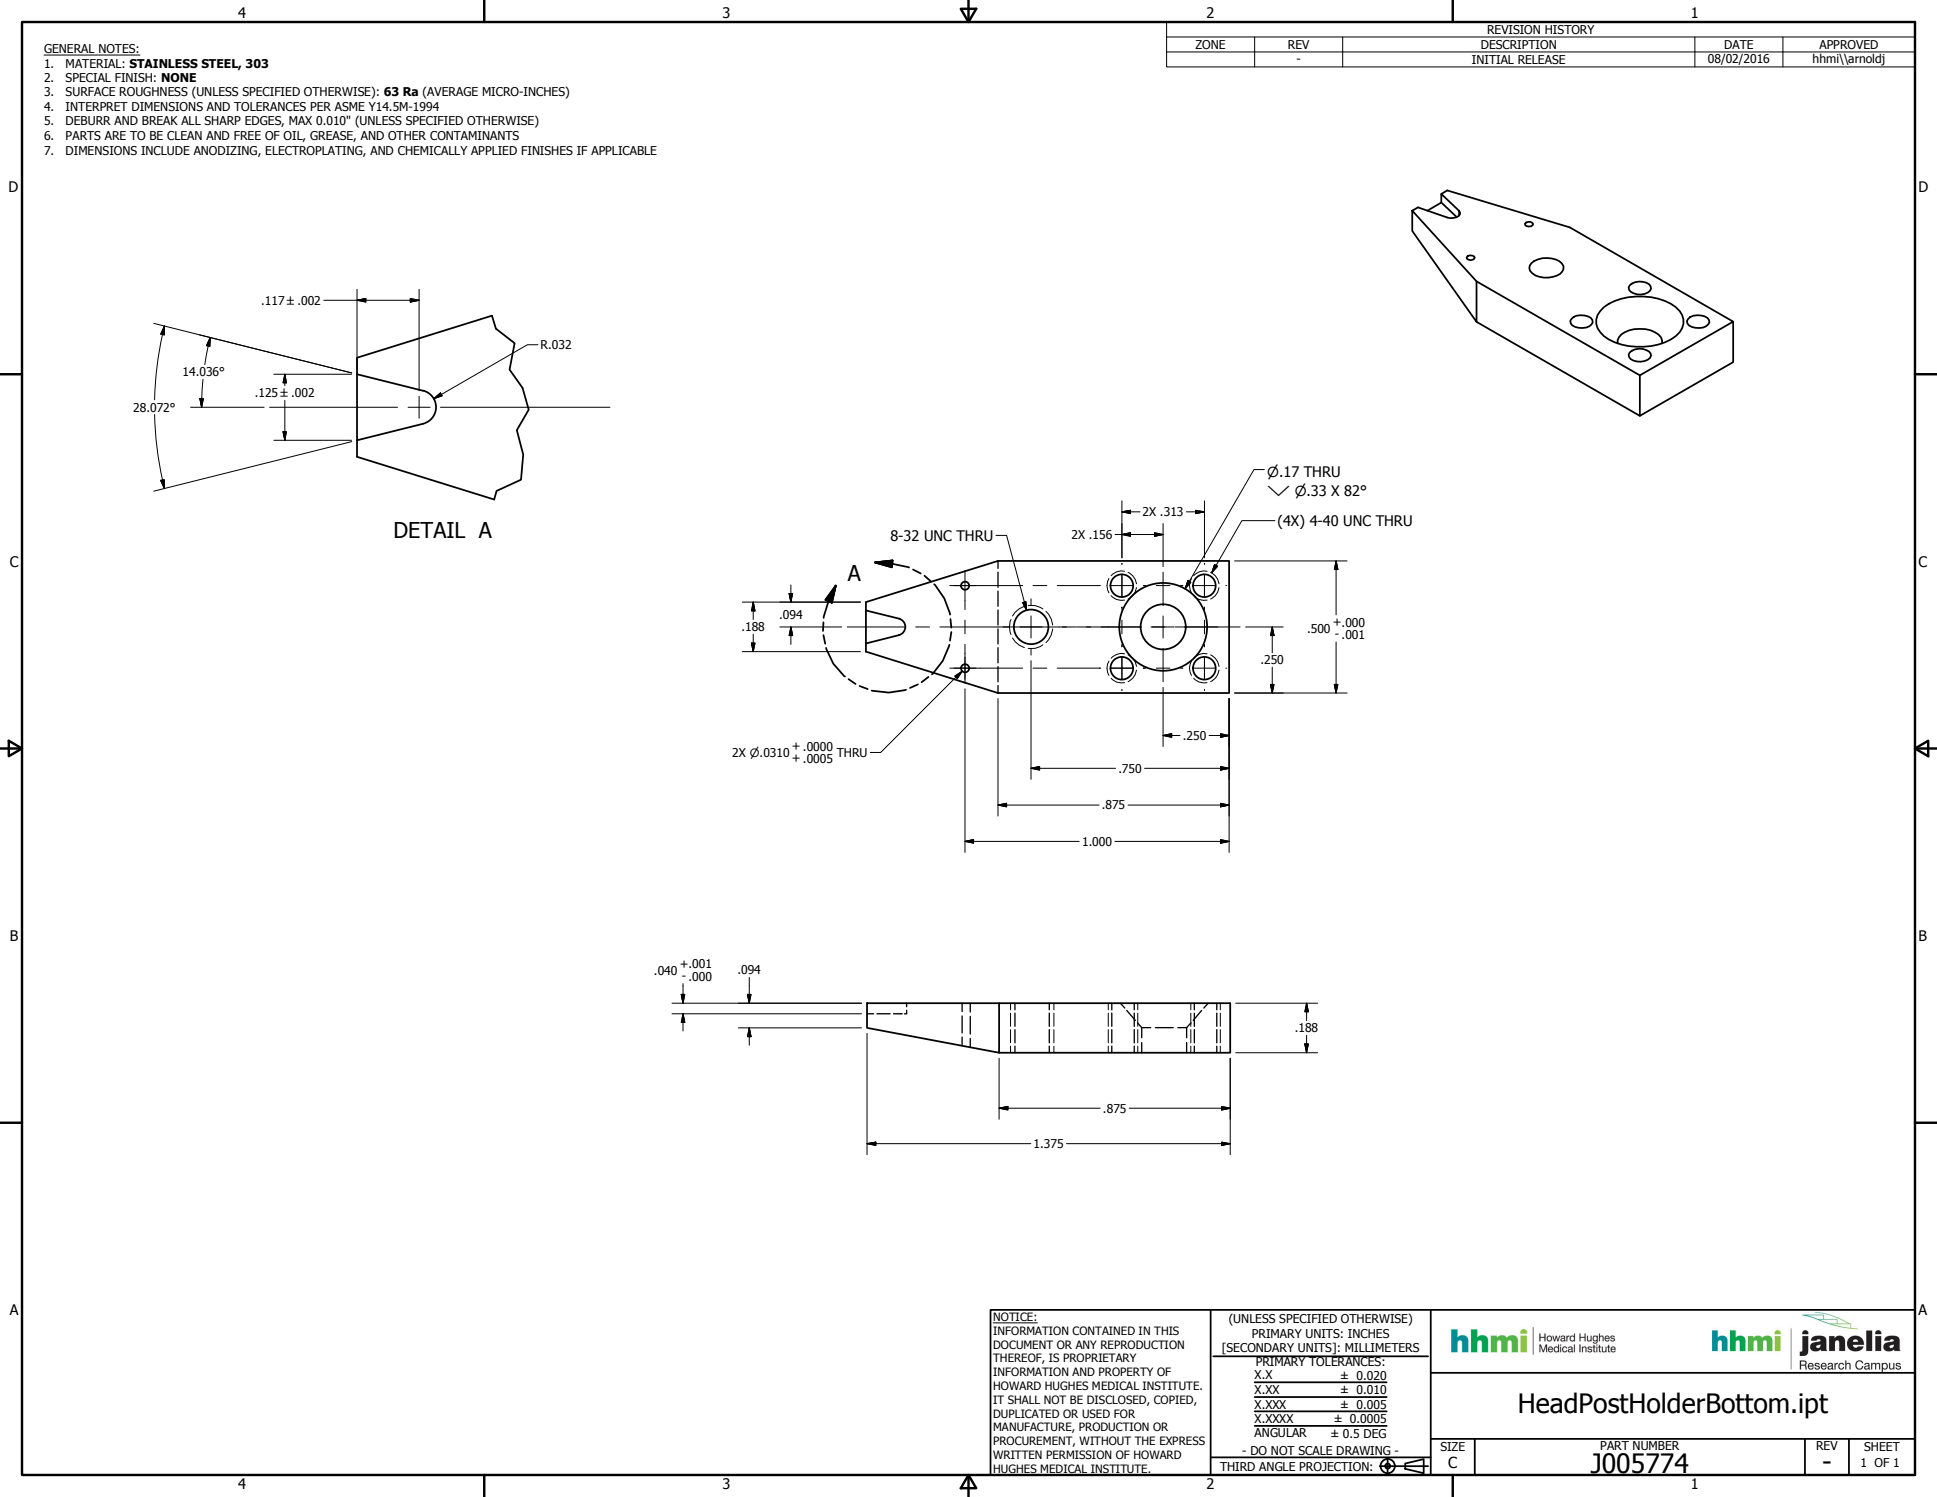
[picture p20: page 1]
DETAIL A; PART NUMBER; SIZE; REV; SHEET; 1 OF 1 THIRD ANGLE PROJECTION:; ± 0.020 ± 0.010 ± 0.005 ± 0.0005 ± 0.5 DEG; HeadPostHolderBottom.ipt; REVISION HISTORY; ZONE; DESCRIPTION; DATE; APPROVED; INITIAL RELEASE; hhmi\\arnoldj; (4X) 4-40 UNC THRU; P.17 THRU Y P.33 X 82°; 8-32 UNC THRU; THRU

GENERAL NOTES:
1. MATERIAL: STAINLESS STEEL, 303
2. SPECIAL FINISH: NONE
3. SURFACE ROUGHNESS (UNLESS SPECIFIED OTHERWISE): 63 Ra (AVERAGE MICRO-INCHES)
4. INTERPRET DIMENSIONS AND TOLERANCES PER ASME Y14.5M-1994
5. DEBURR AND BREAK ALL SHARP EDGES, MAX 0.010" (UNLESS SPECIFIED OTHERWISE)
6. PARTS ARE TO BE CLEAN AND FREE OF OIL, GREASE, AND OTHER CONTAMINANTS
7. DIMENSIONS INCLUDE ANODIZING, ELECTROPLATING, AND CHEMICALLY APPLIED FINISHES IF APPLICABLE

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

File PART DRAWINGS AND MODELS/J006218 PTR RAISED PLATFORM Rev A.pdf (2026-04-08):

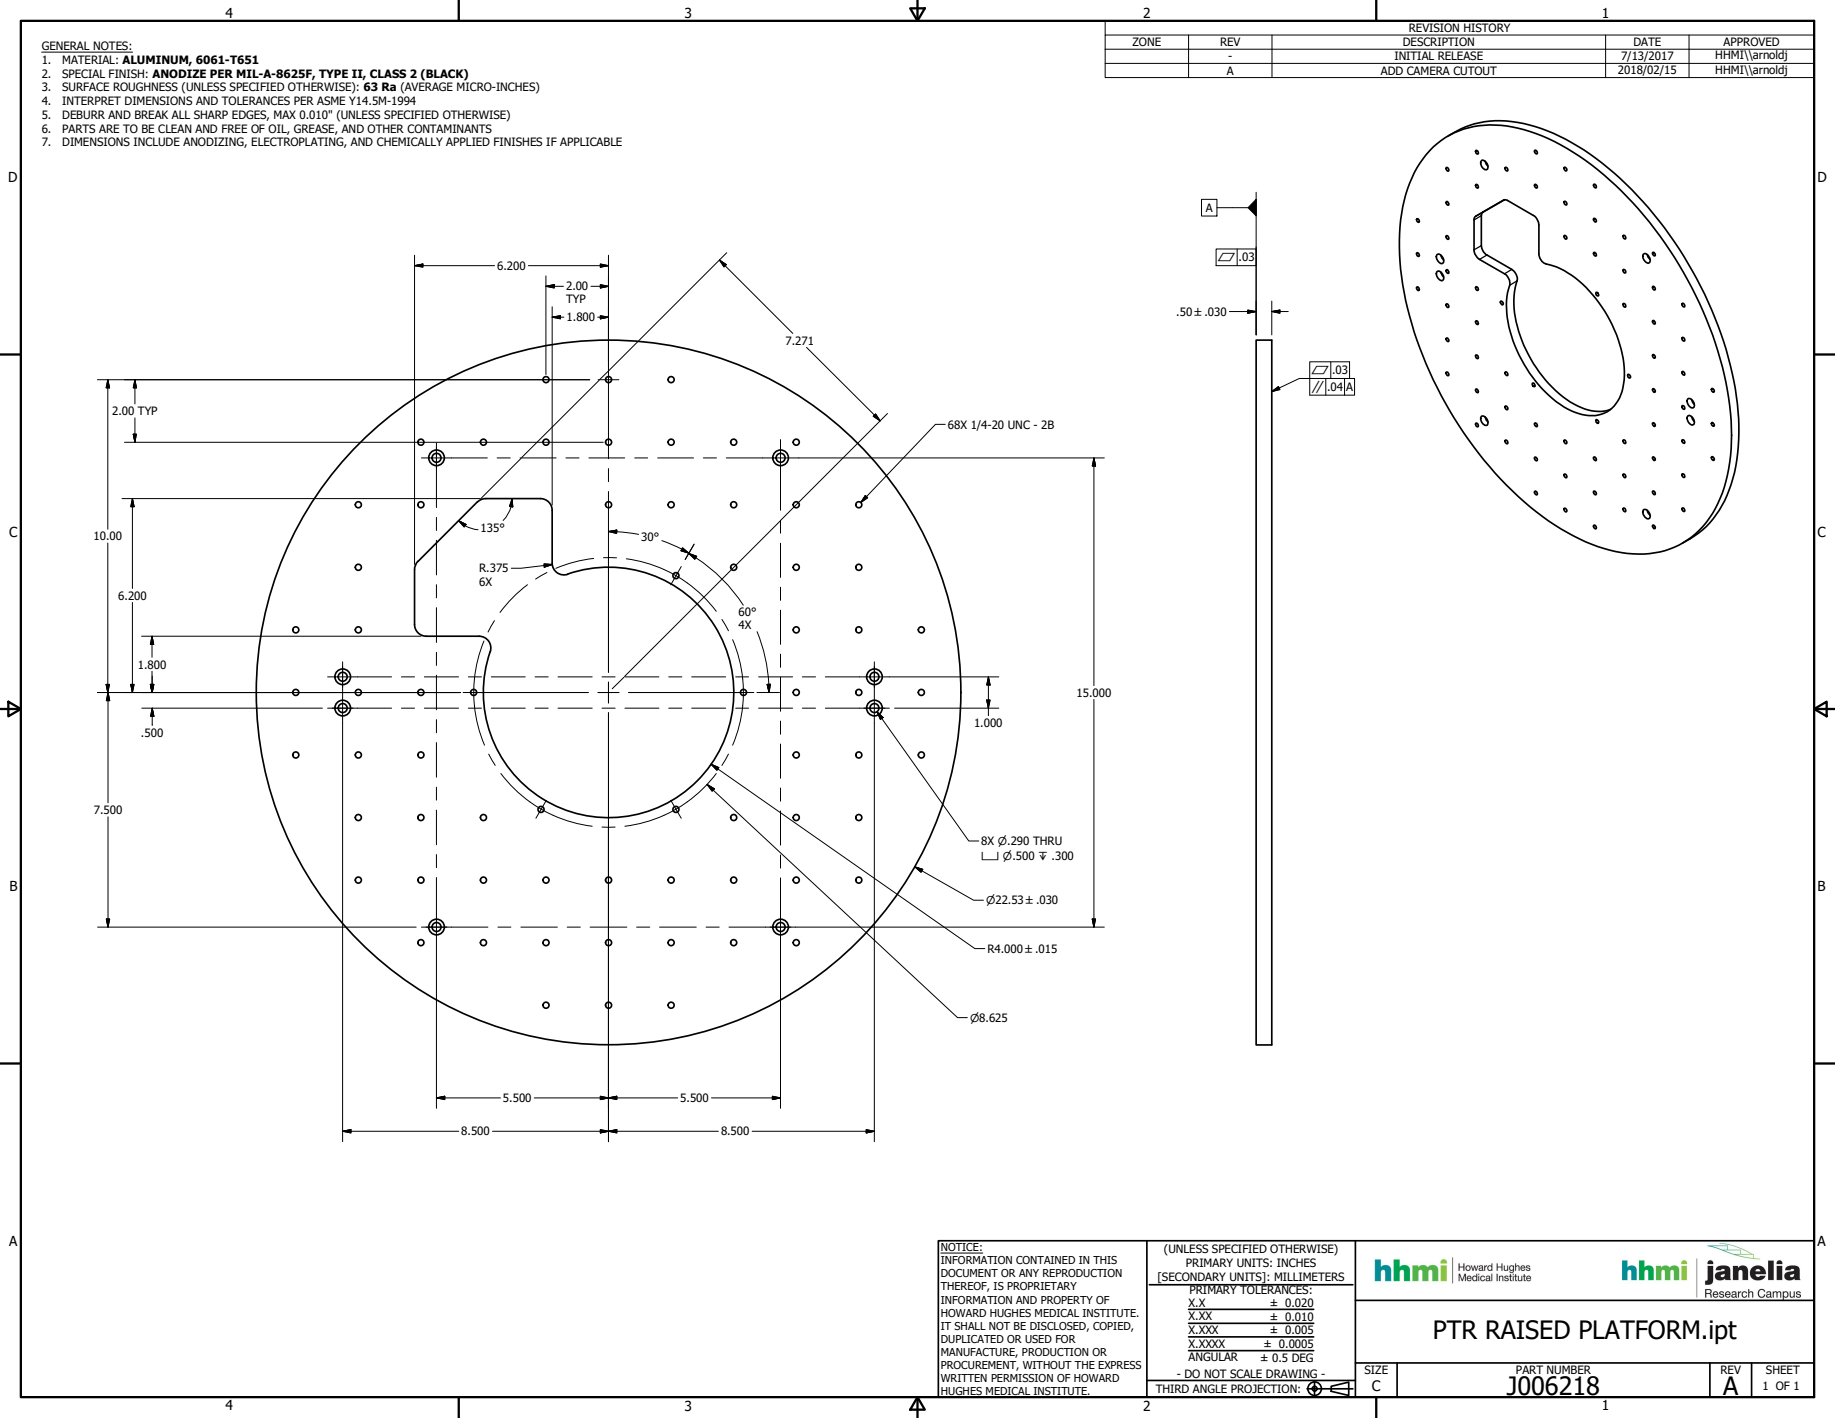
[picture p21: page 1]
PART NUMBER; 1 OF 1 THIRD ANGLE PROJECTION:; ± 0.020 ± 0.010 ± 0.005 ± 0.0005 ± 0.5 DEG; REVISION HISTORY; 2.00 TYP; 68X 1/4-20 UNC - 2B

GENERAL NOTES:
1. MATERIAL: ALUMINUM, 6061-T651
2. SPECIAL FINISH: ANODIZE PER MIL-A-8625F, TYPE II, CLASS 2 (BLACK)
3. SURFACE ROUGHNESS (UNLESS SPECIFIED OTHERWISE): 63 Ra (AVERAGE MICRO-INCHES)
4. INTERPRET DIMENSIONS AND TOLERANCES PER ASME Y14.5M-1994
5. DEBURR AND BREAK ALL SHARP EDGES, MAX 0.010" (UNLESS SPECIFIED OTHERWISE)
6. PARTS ARE TO BE CLEAN AND FREE OF OIL, GREASE, AND OTHER CONTAMINANTS
7. DIMENSIONS INCLUDE ANODIZING, ELECTROPLATING, AND CHEMICALLY APPLIED FINISHES IF APPLICABLE

ZONE | REV | DESCRIPTION | DATE | APPROVED

- | INITIAL RELEASE | 7/13/2017 | HHMI\\arnoldj
A | ADD CAMERA CUTOUT | 2018/02/15 | HHMI\\arnoldj

 .03
 .04 A

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

PTR RAISED PLATFORM.ipt
